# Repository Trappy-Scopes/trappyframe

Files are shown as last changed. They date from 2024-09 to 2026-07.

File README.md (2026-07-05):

# trappyframe

`trappyframe` is a **low-cost** and **open-source** microscopy system that is **highly customisable**. It is an inverted **low-magnification system** (1-2X) that is built on a 3D printed opto-mechanical cage system, simple optics, and the Raspberry Pi Hardware ecosystem. This system was **build for parallelisation**. Multiple units can be assembled, mounted, and operated in parallel. The microscope can be printed and assembled in any laboratory/school/home with a few simple tools. 

The microscope is primarily designed to **track motile algae**. However, it can be used as it is or customised for any general microscopy requiremnt. 

Instructions on parallelisation, including the assmmbly of a Raspberry Pi cluster/bramble can be found in the parallel project [Trappy-Scopes/raspberry_shrub](https://github.com/Trappy-Scopes/raspberry_shrub/tree/main). The control layer software can be found in the parallel project [Trappy-Scopes/trappyscopes](https://github.com/Trappy-Scopes/trappyscopes) and instructions to configure it for `trappyframe` can be found in the [here](docs/notes/software_configuration.md).

## Microscope Frame

Out compact microscopy frame can be 3D-printed with a commercial 3D printer and be parallelised.

<table align="center" border="0" cellspacing="20">
  <tr>
    <td align="center" border="0">
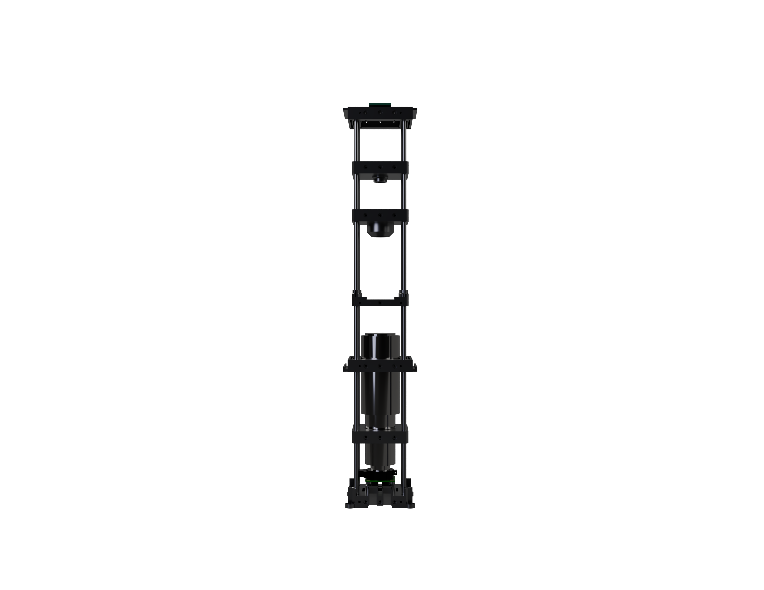
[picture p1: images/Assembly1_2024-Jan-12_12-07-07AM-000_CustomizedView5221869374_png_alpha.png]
        
      </a><br/><b>Single Unit</b>
    </td>
    <td align="center">
        
        </a><br/><b>Parallelised Cluster</b>
</table>

## Specialised Cage System

<table align="center" border="0" cellspacing="20" style="width:100%;">
  <colgroup>
    <col style="width:35%;">
    <col style="width:65%;">
  </colgroup>
  <tr>
    <td align="center">
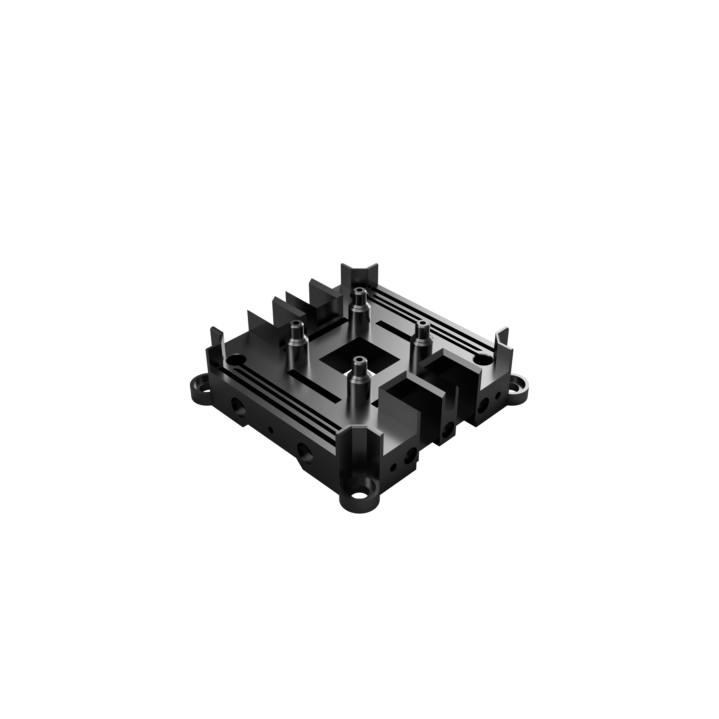
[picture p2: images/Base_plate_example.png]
Base plate
      <br/>
    </td>
    <td align="left">
      <h4>Camera mount base plate</h4>
      Specialised cage-system components that serve specific purposes like camera mounting, sample holding, etc rely on flexure mechanisms to hold position. This makes assembly simpler by eliminating the need for thread inserts.
    </td>
  </tr>
</table>

## Build on a standard block template

A standard block template was used  to design every component. The templates support a **60mm cage footprint** with **6mm support rods**.

<iframe
  style="width:100%; height:400px; border:none;"
  srcdoc='
    <script type="module" src="https://unpkg.com/@google/model-viewer/dist/model-viewer.min.js"></script>
    <model-viewer
      src="https://raw.githubusercontent.com/Trappy-Scopes/trappyframe/69a5afcf80012a002b0ecb415eb8199e39919581/trappyframe/block_templates/trappyframe_60mm_component_template_v1.glb"
      alt="60mm component template"
      auto-rotate
      camera-controls
      shadow-intensity="0.4"
      exposure="1"
      style="width:100%; height:100%; background-color:transparent;">
    </model-viewer>
  '>
</iframe>

|                          |                                  |                              |
| ------------------------ | -------------------------------- | ---------------------------- |
| Component Block Template | Component Block Template w Studs | Frame Support Block Template |

## Magnetic box to keep away stray light

## Scope of this repository

1. Repository for the 3D models of cage system components: [trappyframe](/trappyframe)
2. Repository for other bill of materials (BOM): [BOM](/docs/notes/bom.md)
3. Easy assembly instructions: [Assembly Instructions](/docs/notes/assembly_instructions.md)

## Frame Components

Notes:

1. The rod holes are currently set to 6.3mm corresponding to the specific 3D printer and nozzle sizes. Ity might have to be modified based on your settings.
2. 3D printer used: Bambu Lab X1E 0.4mm nozzle.
3. Filament of choice: PLA Black 3D.

| No   | Peripheral                                | Filename                                                     | Latest versionª |
| ---- | ----------------------------------------- | ------------------------------------------------------------ | --------------- |
| -    | **TOP - Illumination controller**         | -                                                            | -               |
| 1    | Top plate (frame support)                 | [Top Plate w Magnets(FSSBTv2) v13.stl]("frame/Top%20Plate%20w%20Magnets(FSSBTv2)%20v13.stl") | 13              |
| 2    | LED mount plate                           | [SBTv2 LED mount w studs v11.stl](frame/SBTv2%20LED%20mount%20w%20studs%20v11.stl) | 11              |
| 3    | Condensor mount plate                     | [Condensor Mount 25mm wo tube  (SBTv2) v3 6.3mm rod holes.stl](/frame/Condensor%20Mount%2025mm%20wo%20tube%20%20(SBTv2)%20v3%206.3mm%20rod%20holes.stl) | 3               |
| 4    | Sample stage plate                        | [Sample Mount Agile w Small magnets (SBTv2) v7.stl](/frame/Sample%20Mount%20Agile%20w%20Small%20magnets%20(SBTv2)%20v7.stl) | 7               |
| 5    | Mid plate (frame support)                 | [Mid Plate Magnets 6.3mm  (FSSBTv2) v14.stl](/frame/Mid%20Plate%20Magnets%206.3mm%20%20(FSSBTv2)%20v14.stl) | 14              |
| 6    | Tube lens upper mount plate               | [Tube Lens Holder 6.3 upper (SBTv2) v2.stl](/frame/Tube%20Lens%20Holder%206.3%20upper%20(SBTv2)%20v2.stl) | 2               |
| 7    | Tube lens lower mount plate               | [Tube Lens Holder 6.3 lower (SBTv2) v3.stl](/frame/Tube%20Lens%20Holder%206.3%20lower%20(SBTv2)%20v3.stl) | 3               |
| 8    | Base plate w camera mount (frame support) | [Base Plate 6.3mm (FSSBTv3) v2.stl](/frame/Base%20Plate%206.3mm%20(FSSBTv3)%20v2.stl) | 2               |
| -    | **BOTTOM - Breadboard**                   | [ThorLabs MB3060/M](https://www.thorlabs.com/thorproduct.cfm?partnumber=MB3060/M) | -               |

ª : the version numbers correspond to the filename version for Fusion 365. 

## Standard Block Templates

The parts are designed from standard design blocks. Two different versions exist. One for the normal parts, and one for parts which support the rods, and the box for the frame.

| No   | Peripheral Block Template                     | Filename                                      | Latest versionª |
| ---- | --------------------------------------------- | --------------------------------------------- | --------------- |
| 1    | Standard block template (SBT)                 | [SBTv2 v3.stl](frame_templates/SBTv2.stl)     | 2               |
| 2    | Frame support standard block template (FSSBT) | [FSSBTv3 v3.stl](frame_templates/FSSBTv3.stl) | 3               |

ª : the version numbers correspond to the filename version for Fusion 365.

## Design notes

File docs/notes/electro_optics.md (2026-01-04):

# Electronics & Optics

Optics and electronics can be customised to the specific needs. This note in particular covers the use of a commercial Tube-Lens as a low-magnification objective. The Tube Lens is coupled to a **Raspberry Pi HQ Camera**, which connects to a **Raspberry Pi SoC**.  For electronics, we describe a universal controller framework based on the Raspberry Pi pico microcontroller that can be used to control illumination, and temperature senosors. 

The microcontroller plateform allows for arbitrary customisation. This topic is developed separately in the [Trappy-Scopes/electronics](https://github.com/Trappy-Scopes/electronics) which contains instructions on how to assemble very simple eletronic circuits. Most of the magic happens in code and the `micropython` firmware for the microcontroller platform can be found in the [Trappy-Scopes/pico_firmware](https://github.com/Trappy-Scopes/pico_firmware).

```mermaid
---
title: Components that are covered in this article
config:
  layout: default
---

graph TD
	RPi(Raspberry Pi SoC) <--CSI Cable--> HQ(("Raspberry Pi<br>HQ Camera")) <--> TubeLens([Tube Lens])
	RPi <--USB cable--> pico[Raspberry Pi<br>Pico] 
	pico --> LED((LED))
	pico --> tandh((Temperature<br>Sensor))
```

# Raspberry Pi Ecosystem Components

All the information can be found here: https://www.raspberrypi.com/. The website also featues offical resellers specific to all countries.

## System on Chip (Soc)

We use Raspberry Pi 4B, however Raspberry Pi 5 and to some extent lower models are also fine. We recommend using a high RAM version — 8GB. This needs to be coupled with a microSD card, we reommmend a decent 128GB card. Higher memory can be unstable, but upto 128GB works well and has been extensively tested. We will also need connector cables, which are listed in the Bill of Materials page.

https://www.raspberrypi.com/products/raspberry-pi-4-model-b/

1. [SoC Product homepage](https://www.raspberrypi.com/products/raspberry-pi-4-model-b/)

## HQ Camera



1. [Camera Product Guide](https://www.raspberrypi.com/products/raspberry-pi-high-quality-camera/)
2. [Camera CSI connector cable](https://www.raspberrypi.com/products/camera-cable/)

## Pico microcontroller board

We use the pico series 1 board, but newer version boards should also work well. To make the code compatible with other versions, or boards, please remeber to update the pin assignments for that particular board. 

pico board

1. [Product Homepage](https://www.raspberrypi.com/products/raspberry-pi-pico/)

# Temperature Sensors

1. 

## Optics

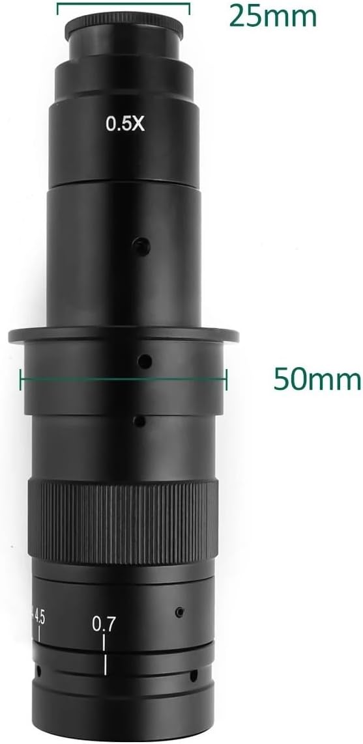
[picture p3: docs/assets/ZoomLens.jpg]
ZoomLens


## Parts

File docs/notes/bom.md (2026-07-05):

<script type="module" src="https://unpkg.com/@google/model-viewer/dist/model-viewer.min.js"></script>

<script type="module" src="https://unpkg.com/@google/model-viewer/dist/model-viewer.min.js"></script>

<table align="center" border="0" cellspacing="20" style="width:100%; max-width:1400px;">
  <tr>
    <td align="center" style="width:33%;">
      <model-viewer
        src="https://raw.githubusercontent.com/Trappy-Scopes/trappyframe/69a5afcf80012a002b0ecb415eb8199e39919581/trappyframe/block_templates/trappyframe_60mm_component_template_v1.glb"
        alt="60mm component template"
        auto-rotate
        camera-controls
        camera-orbit="0deg 75deg 60%"
        field-of-view="25deg"
        shadow-intensity="0.4"
        style="display:block; width:100%; height:60vh; min-height:400px; background-color:transparent;">
      </model-viewer>
      <br/><b>Component Block Template</b>
    </td>
    <td align="center" style="width:33%;">
      <model-viewer
        src="PASTE_RAW_URL_HERE.glb"
        alt="Component block template with studs"
        auto-rotate
        camera-controls
        camera-orbit="0deg 75deg 60%"
        field-of-view="25deg"
        shadow-intensity="0.4"
        style="display:block; width:100%; height:60vh; min-height:400px; background-color:transparent;">
      </model-viewer>
      <br/><b>Component Block Template w Studs</b>
    </td>
    <td align="center" style="width:33%;">
      <model-viewer
        src="PASTE_RAW_URL_HERE.glb"
        alt="Frame support block template"
        auto-rotate
        camera-controls
        camera-orbit="0deg 75deg 60%"
        field-of-view="25deg"
        shadow-intensity="0.4"
        style="display:block; width:100%; height:60vh; min-height:400px; background-color:transparent;">
      </model-viewer>
      <br/><b>Frame Support Block Template</b>
    </td>
  </tr>
</table>

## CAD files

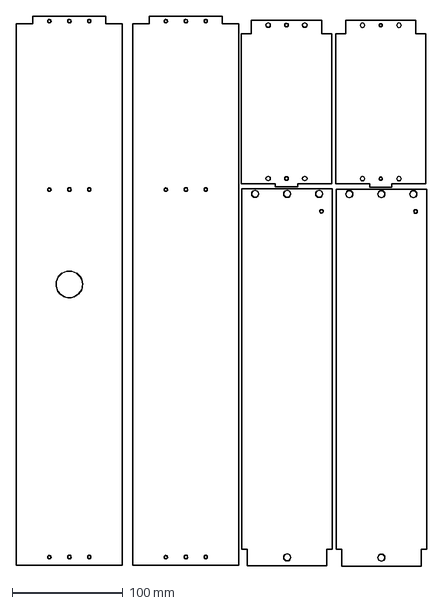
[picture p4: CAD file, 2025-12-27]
box1_sketch_v1.dxf
371.2 x 497.5 mm

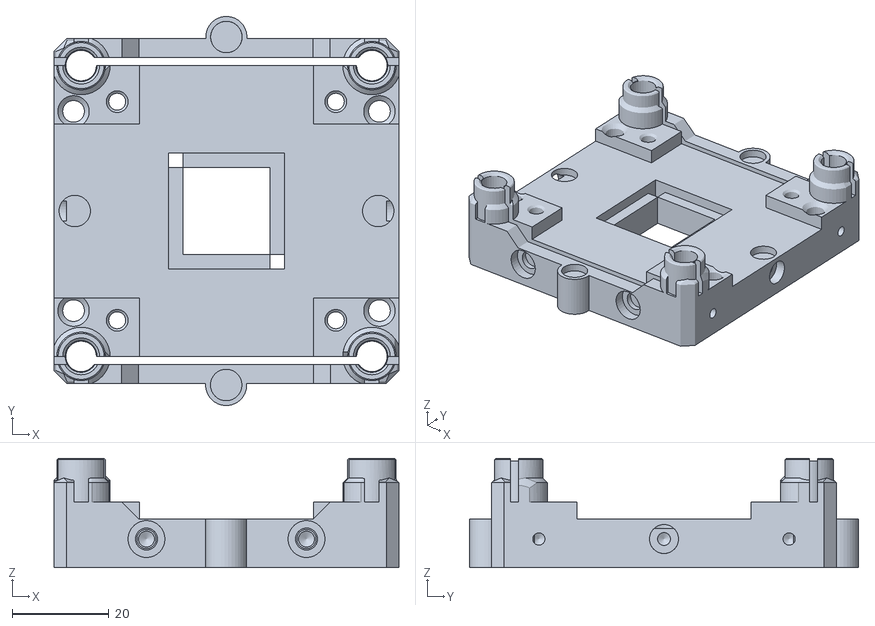
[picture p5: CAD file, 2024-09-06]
frame/Sample Mount Agile w Small magnets (SBTv2) v7.stl
71.1 x 80.3 x 22.5

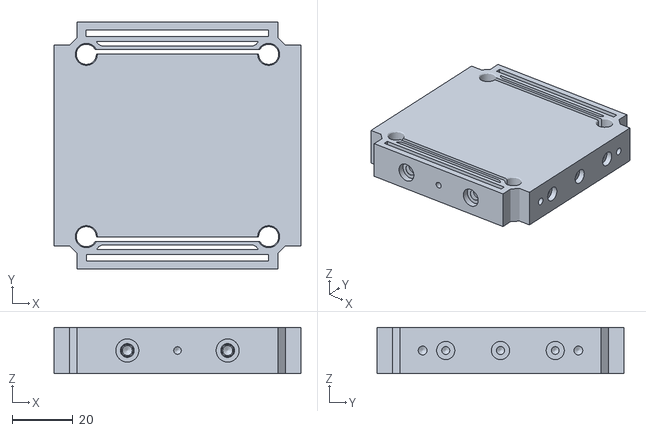
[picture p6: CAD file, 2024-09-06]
frame_templates/FSSBTv3.stl
81.3 x 81.3 x 15.2

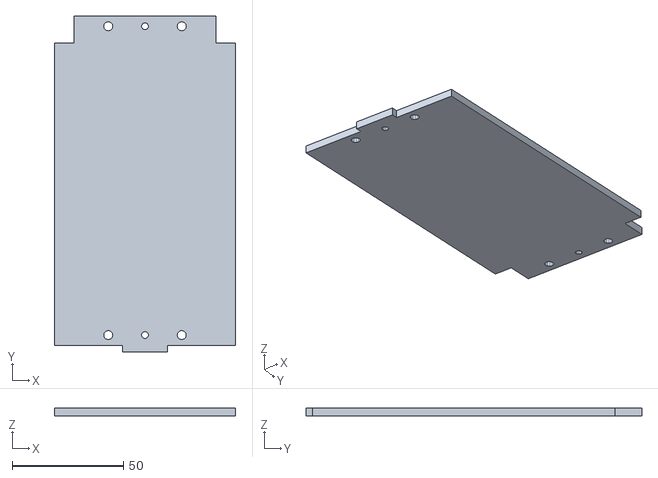
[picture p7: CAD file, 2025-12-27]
trappyframe/trappybox/LR_bottom_panel/STLs/LR_bottom_panel_solid_decal v7.stl
81.5 x 151.0 x 3.50

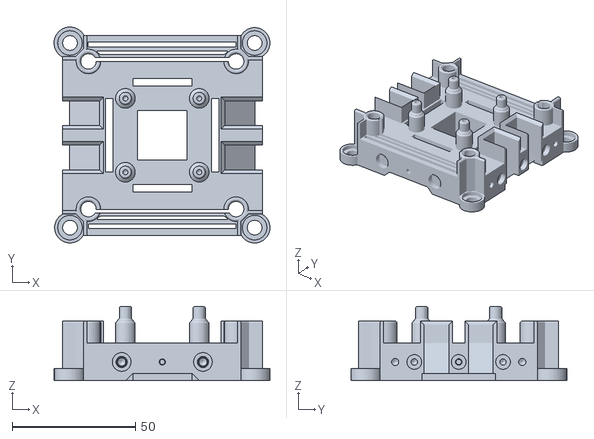
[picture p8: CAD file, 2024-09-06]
frame/Base Plate 6.3mm (FSSBTv3) v2.stl
87.7 x 87.7 x 30.2

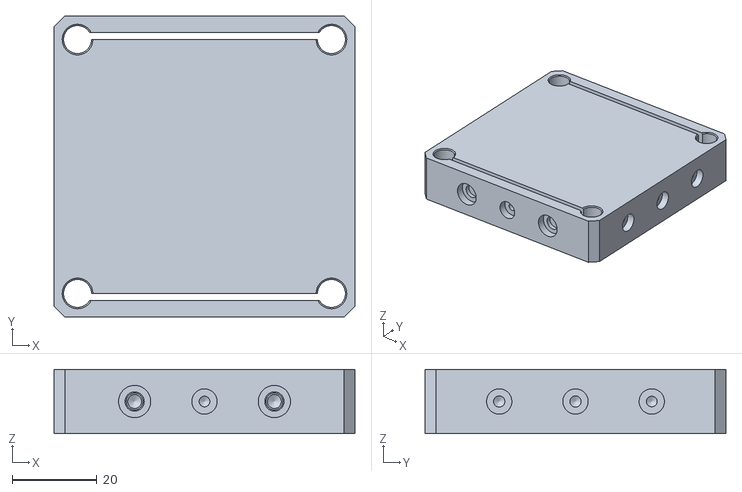
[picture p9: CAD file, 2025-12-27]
trappyframe/block_templates/trappyframe_60mm_component_template_v1.stl
71.1 x 71.1 x 15.2

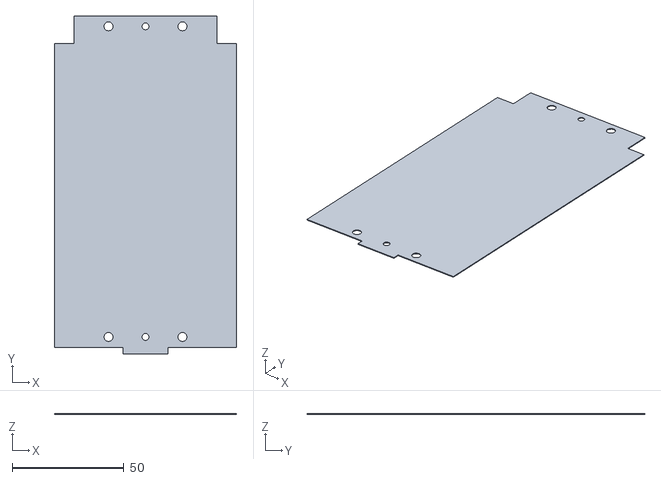
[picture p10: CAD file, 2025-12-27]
trappyframe/trappybox/LR_bottom_panel/STLs/LR_bottom_panel_solid v2.stl
81.5 x 151.0 x 0.35

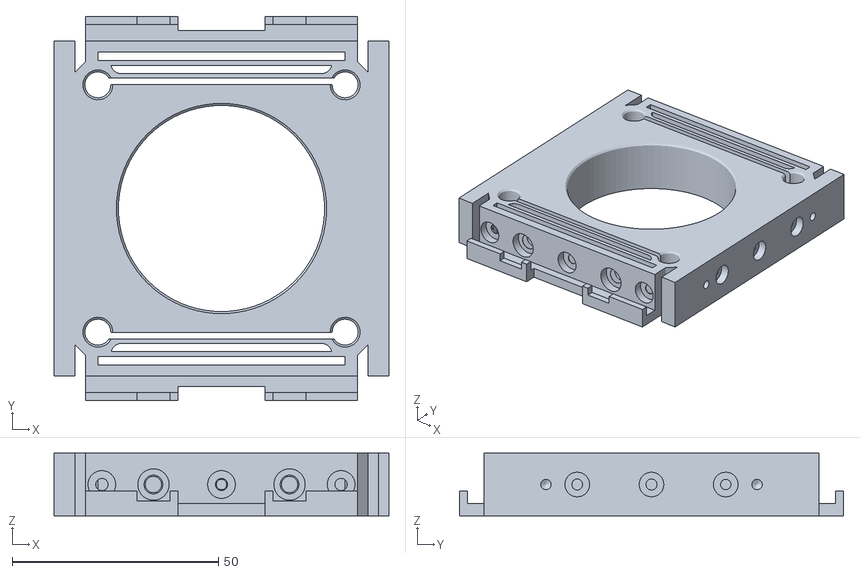
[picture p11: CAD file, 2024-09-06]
frame/Mid Plate Magnets 6.3mm (FSSBTv2) v14.stl
81.3 x 93.3 x 15.2

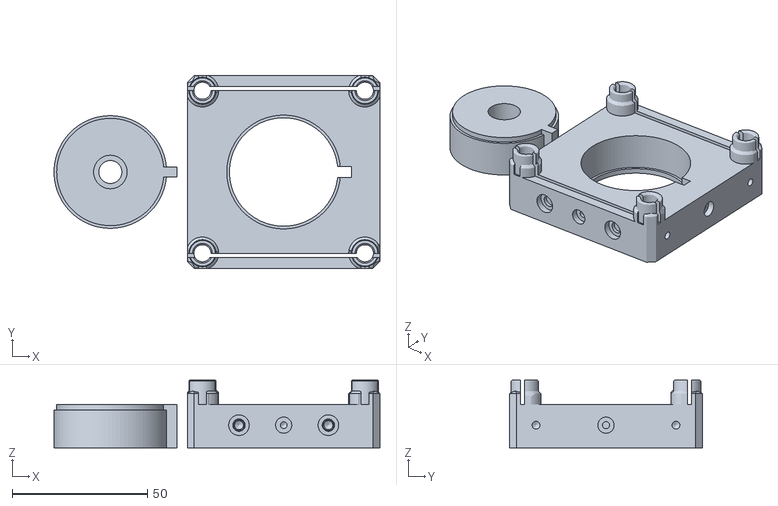
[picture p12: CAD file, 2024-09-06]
frame/SBTv2 LED mount w studs v11.stl
120.4 x 71.1 x 25.0

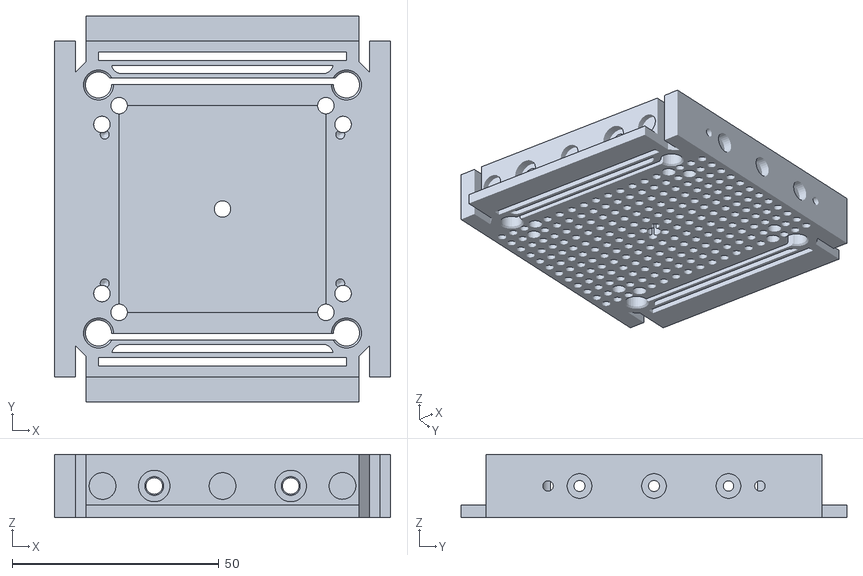
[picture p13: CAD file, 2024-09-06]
frame/Top Plate w Magnets(FSSBTv2) v13.stl
81.3 x 93.3 x 15.2

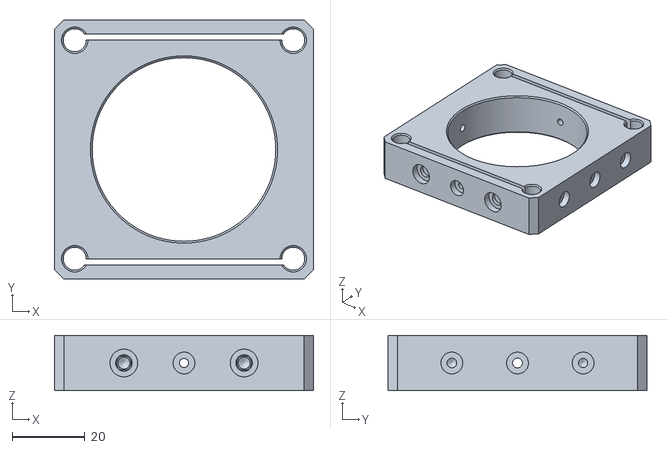
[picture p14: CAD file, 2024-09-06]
frame/Tube Lens Holder 6.3 upper (SBTv2) v2.stl
71.1 x 71.1 x 15.2

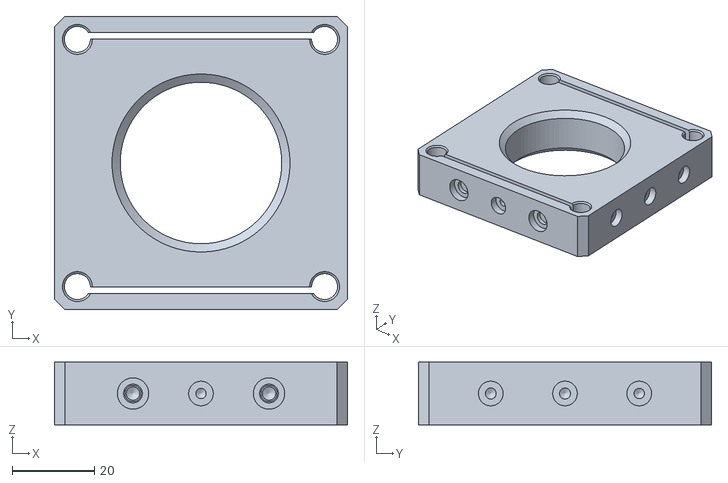
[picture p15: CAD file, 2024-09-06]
frame/Tube Lens Holder 6.3 lower (SBTv2) v3.stl
71.1 x 71.1 x 15.2

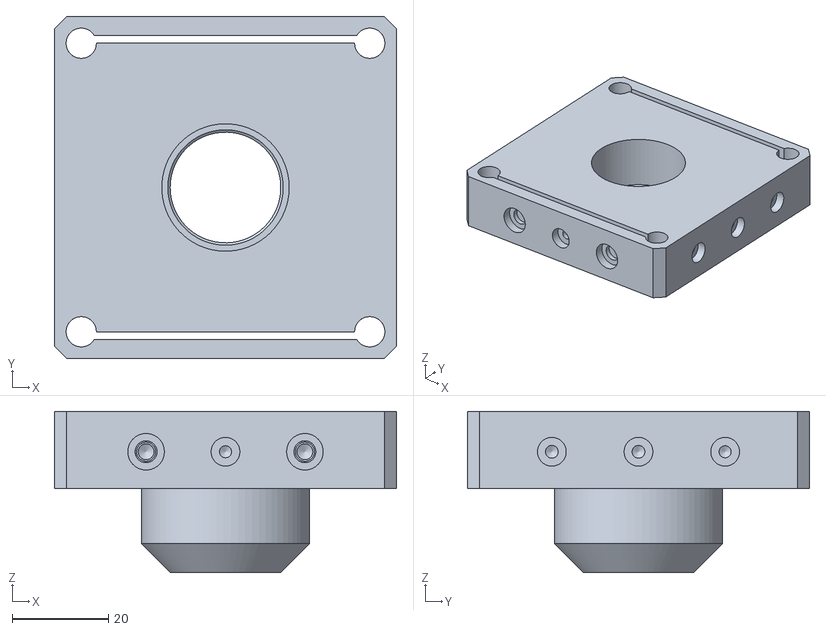
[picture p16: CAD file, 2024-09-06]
frame/Condensor Mount 25mm wo tube (SBTv2) v3 6.3mm rod holes.stl
71.1 x 71.1 x 33.5

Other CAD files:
trappyframe/block_templates/trappyframe_60mm_frame_structure_template_v1.stl
trappyframe/trappybox/LR_bottom_panel/print_files/LR_bottom_panel_solid_decal_v7_printfile.gcode.3mf
trappyframe/block_templates/SBTv2 copy.stl

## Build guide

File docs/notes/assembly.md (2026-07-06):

# Assembly instructions

<script type="module" src="https://ajax.googleapis.com/ajax/libs/model-viewer/4.0.0/model-viewer.min.js"></script>
<center>
<model-viewer
        src="../../assets/Cluster v4.gltf"
        alt="60mm component template"
        auto-rotate
        camera-controls
        camera-orbit="0deg 75deg 60%"
        field-of-view="25deg"
        shadow-intensity="0.4"
        style="display:block; width:100%; height:60vh; min-height:400px; background-color:transparent;">
</model-viewer>

---

How to assemble the trappy-scopes microscopes in easy to follow 100 steps:

1. Take a **baseplate** and mount the Rasperry Pi HQ Camera on the pegs using M2-10mm screws (X4). Remove the tripod mount from the camera as it is not required. We recommend long CSI cables (24" from Adafruit 1731). Pass the CSI cable from the slits to the camera connector. Prefer using a side which is adjacent to the **flexures**. Connect the cable (it should pass under the Baseplate and to the camera. Do not twist the cable and handle it gently.) The connectors (shiny-side) should face up towards you when you connect them to the camera.

2. Take four 6mm diameter 50cm Stainless steel rods. You can get your own cheaper ones or buy from ThorLabs. Mount them to the baseplate and tighten the flexures using M4-10mm screws. Make sure that there is no imbalance and the rods are evently inserted. You should consider additional steps to improve rod adhesion to the baseplate:
	1. Use a bit of stanard electrical tape at the end of the rods to improve fitting.
	2. Additional headless-screws that can be mounted (holes already inbuilt.) TODO-add screw specifications
	3. Use a strong glue at the baseplate to bond the rods to the plate.
	
3. Mount the baseplate on an **M6 breadboard** temporrily to aid assembly. We recommend a smaller breadboard for the assemby.  Subsequently the unit should be transported to its final place after certain assembly steps. M6-10mm screws are recommended for this.

4. Add the **Lower-Tube lens mount** (has a smaller central hole compared to the Upper-Tube mount) to the frame from the top (The flexure side should align with the flexure side of the baseplate).

5. Add the **zoomlens** to the mount without taking of its covers.

6. Add the **Upper-zoom lens mount**. The zoomlens should snuggly align with mounts. We will connect it to the camera and align it later.

7. Add the **midplate** to the frame and place it approximately near the knulred ring of the zoomlens.

8. Assemble the **sample stage**:
	1. The magentic mount sample stage needs to be assembled beforehand. It used four 1.9mm high 6.2mm diameter magnets in a cylinder form-factor. The magnets should directly fit in their respective holes. But since 3D printing is not an exact science, we can use the help of some glue. Use only sufficiently enough glue and fit the magents in place. Decide which pole should stay up and stick with it! Do not randomly place the magents. 
	2. If you used glue, let it dry for a sufficent time. Clean the stage of any access glue beforehand.
	3. If you plan to use any additional peripherals that mount from below, you should also install the magents under the stage in the same prescribed way.
	4. Add the sample mount to the assembly (align the flexures!). Z-position is irrelvant. Place it above the tubelens ofcourse.
	
9. Add the **asphere/condensor mount** to the assembly (align the flexures!). Check this part specifically for imperfections on the inside. Clean it, if required.

10. Add the **ED/illumination mount** to the assembly sans the LED clip. Pick a conventional side for the slit and stick with it (extra careful in aligning the flexures! Todo-explain more.

11. Assemble the **top plate**:
	1. Add two magnets (the centre should be sufficient). Follow the same rules as the **sample stage**.
	2. Add it to the saaembly.
	
12. Attaching the camera to the tubelens: it helps a lot to be clean. Clean the dust. Wash your hands and wear gloves if you can!
	1. Lift the componets gently until there is some space bwtween the camer and the tubelens.
	2. Remove the caps first from the tubelens and then the camera. Bring the two componets close and they should perfectly align! If they don't then you made a mistake somewhere. Cover the camera immediately and start again. Remember to choose the apropriate adapter (the HQ camera comes with both C and CS mounts.)
	3. Rotate the tubelens very slowly as access speed causes friction and that chips off small pieces of metal that contaminate the camera surface.
	4. Turn until you can't and ensure that the tube lens is firmly mounted on the camera.
	5. Move the upper and lower zoomlens mount plate to fix the tubelens properly.
	6. Use eight M4-10mm screws to fix both the plates in position.
	7. Sometime, the alignment mark on the tubelens gets shaded by the box, so better add a haptic cue, like a piece of coarse tape that you can feel.
13. Assmble the **trappybox side sections** (the long ones) (M3-5mm screws):
	1. Take the back-side and mount it on the topplate (central and a side screw).
	2. Now add the central screw on the baseplate. Screwing is difficult but not immpossible. If its too difficult for you, then leave it for the end!
	3. Now try and align the midplate with its respective screw holes (first the center and then a side one).
	4. Repeat these steps for the front side  (long one)!
	5. Add extra screws to improve the stability, these many should work fine.
	
	6. With the last steps, we have also properly aligned the midplate and the topplate, so fix them with M4-5mm screws.
	7. Unscrew the scope assembly from the breadboard (all four screws). But keep the screws there. Release the screws that connect the box to the baseplate to release some tension. Now attach the small flaps with one M3-5mm screw each on the baseplate. Do not tighten it, keep them such that they are like a flap. You can skip this step if you have no space constrains!
	8. No put the scope on its designated position and tighten the M6 screws again! Tighten them well! It's permanent. You should be able to access the screws through the flaps.
	9. Pass the CSI cable to the SoC (RPi 4B or smth) and tug the extra cable between the tubelens and the box. Now tighten the small portions of the box and fix them. If you have many CSI cables that are overlapping, insulate them further with Aluminium foil or something, or there will be a lot of interferance.
	10. Add the pico board that connects to LEDs and the temperature sensor on top of the topplate. There is a breadboard and standard M2.6 screws should work well.
	11. Now add an appropriate temperature and humidity sensor (swinging near the sample stage and run the wires through the top plate flexure on your left side).
	12. On the right side. Add a closed Rod support clamp and use two M3-20mm screws and M3 nuts to secure them.
	13. Assembling the LED climp complex:
	   1. TODO
	14. Connect the sensors and LEDs to the RPi Pico based controller. Make sure to connect to the right pins and keep the connections tight.

# Models

<!-- Use it like any other HTML element -->
<model-viewer alt="Neil Armstrong's Spacesuit from the Smithsonian Digitization Programs Office and National Air and Space Museum" src="Astronaut-Unlit.glb" shadow-intensity="1" camera-controls touch-action="pan-y" style="width: 400px; height: 400px;"></model-viewer>

<!-- Use it like any other HTML element -->
<model-viewer alt="Neil Armstrong's Spacesuit from the Smithsonian Digitization Programs Office and National Air and Space Museum" src="../assets/mount1.glb" shadow-intensity="1" camera-controls touch-action="pan-y" style="width: 400px; height: 400px;"></model-viewer>

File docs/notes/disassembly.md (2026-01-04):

# Disassembly Instructions

Whether you want to replace the unit, change a part, or reconfigure the scope structure, disassembly is required.

## Disassembling everything

This is easy. Remove all the components one by one. It helps to have the scope mounted on a breadboard.

## To unmount the whole scope without complete disassembly

1. Remove both the left–right bottom box panels.
2. Loosen the bottom M3 screws on the front and back panels so that the acrylic can bend slightly, allowing easier access to the M6 screws holding the scope. Small M3 Allen keys are useful, as the working space is limited.
3. Disconnect the camera cables using a small screwdriver to reach the clamps on both sides.
4. Gently pull the acrylic panels so they do not block the heads of the M6 screws, then loosen the M6 screws completely. Move diagonally to prevent stress accumulation on one side: bottom-left → top-right → bottom-right → top-left.

## Change configuration without unmounting

1. Remove the rod clamps.
2. Remove all the M3 screws that connect the box panels to the *Top Plate*.
3. Disconnecting the electronics is not strictly necessary, as the *Top Plate* can be removed while still connected to the LED and the temperature and humidity sensor.
4. Move the parts slowly without applying shear force. Use lubricant if necessary.
